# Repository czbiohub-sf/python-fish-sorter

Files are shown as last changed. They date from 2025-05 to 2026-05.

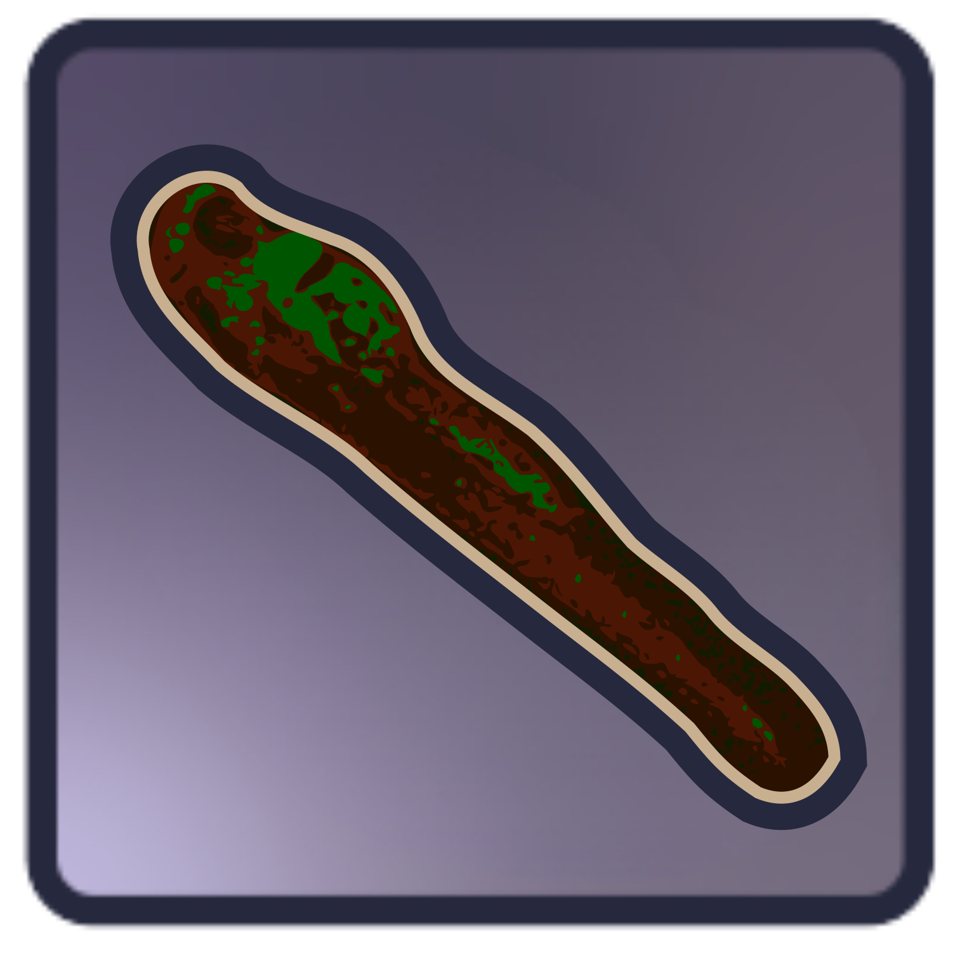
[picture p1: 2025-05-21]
executable/zebrari2.png

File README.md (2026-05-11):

# python-fish-sorter

This repository contains the Python application and custon __python-fish-sorter__ package for control of the Fish Sorter v2 using pymmcore+. Includes image acquisition and processing tools, such as mosaic capture/stitching. 

The Fish Sorter is a custom-built system for automated screening and selection of zebrafish embryos and larvae with desired features of interest. The system is built around a commercial inverted epi-fluorescent microscope for fish imaging, plus additional custom hardware for fish retrieval. 

The fish sorter was developed by the CZ Biohub SF Bioengineering and Jacobo groups.

Maintenance of this repo is the responsibility of Diane Wiener. Plese direct any communication via creation of an Issue at the project repo [here](https://github.com/czbiohub-sf/python-fish-sorter/issues).

This source describes Open Hardware, which is licensed under the CERN-OHL-W v2. Software is licensed under BSD 3-Clause.

Copyright 2025, Chan Zuckerberg Biohub San Francisco.

## Installation with uv

This package uses [uv](https://docs.astral.sh/uv/?utm_source=chatgpt.com) to manage reproducible installs and package dependencies.

The ground truth package lock is based on the software installed for the fish sorter v2 instrument running Windows with Python 3.12.0. The pinned versions are frozen in pyproject.toml + uv.lock.

1. Prerequisites

  * Python 3.12.0 installed on your system.

  * [uv](https://docs.astral.sh/uv/?utm_source=chatgpt.com)

    * Mac/Linux
      ```
        curl -LsSf https://astral.sh/uv/install.sh | sh
      ```
    * Add to PATH if needed
      ```
      echo 'export PATH="$HOME/.local/bin:$PATH"' >> ~/.zprofile
      ```

    * Windows (PowerShell)
      ```
      winget install --id=astral-sh.uv --source=winget -e
      ```
    * Restart PowerShell or add $HOME\.local\bin to PATH

2. Clone the repository

    Clone into your preferred directory (e.g. ~/Documents/GitHub):

    * Mac/Linux
      ```
      cd ~/Documents/GitHub
      git clone https://github.com/<your-org-or-username>/python-fish-sorter.git
      cd python-fish-sorter
      ```

    * Windows (PowerShell)
      ```
      cd $env:USERPROFILE\Documents\GitHub
      git clone https://github.com/<your-org-or-username>/python-fish-sorter.git
      cd python-fish-sorter
      ```
3. First-time setup
   ```
   uv sync
   ```
   
4. Running the project

    Inside the repo:
    ```
    uv run python fish_sorter/GUI/fish_sorter_app.py
    ```

5. Running one-off scripts outside the project

    If you keep helper scripts in a separate repo or folder (e.g. ~/Documents/GitHub/scripts), you can still run them using the fish_sorter environment:
    ```
    cd ~/Documents/GitHub/scripts
    uv --project ../python-fish-sorter run python my_script.py
    ```

    or with an absolute path:
    ```
    uv --project ~/Documents/GitHub/python-fish-sorter run python ~/Documents/GitHub/scripts/my_script.py
    ```

6. Updating dependencies

    Add a new package:
      ```
      uv add somepackage==1.2.3
      uv lock
      ```

    Commit both ```pyproject.toml``` and ```uv.lock```.

    Re-sync environment after changes:
    ```
    uv sync
    ```

7. Notes

    * Always use Python 3.12.

    * The fish sorter v2 instrument environment is the “ground truth.” If you change dependencies, re-lock on instrument first ```uv lock```.

## Local configuration
Follow setup for [napari-micromanager](https://github.com/pymmcore-plus/napari-micromanager) to configure to the specific microscope hardware. 
Micromanager configuration was configured with Micromanager 2.0 20240130. It is recommended to use thate nightly build:
* Use `fish_sorter/GUI/nmm.py` to test run napari-micromanager microscope control
* Use `fish_sorter/GUI/nmm_basic.py` to test run napari-micromanager microscope control with basic ancillary hardware control

An executable file, `fish_sorter.bat`, with icon, `zebrari2_Zbb_icon.ico` are located in the executable folder. 

In case of hardware or software installation differences, the following config files may need updating:
* In case of different Zaber stages, update the stage names in `fish_sorter/configs/hardware/zaber_config.json`
* In case of different micromanager configuration, update `MM_DIR` in `fish_sorter/paths.py`

NOTE: The stage control class in `zaber_controller.py` is intended to work with Zaber's binary library for compatibility with older stages. Newer stages may have compatibility issues with the binary library and require Zaber's ASCII library instead.

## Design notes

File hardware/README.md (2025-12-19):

# Hardware

Includes:
* CAD files for custom CNC components. See BOM (linked below) for material specifications
* CODESYS valve control code for use with Wago valve controllers
* Bill of Materials for off-the-shelf and custom parts

## Useful links
* [Onshape link](https://cad.onshape.com/documents/34757b4dd19d753c9017a122/w/cf503b114c56cf4eae313e87/e/65a73a903388aed1b68b23d7?configuration=default&renderMode=0&uiState=683a2d463e87190e9a255365) to view the full instrument in CAD

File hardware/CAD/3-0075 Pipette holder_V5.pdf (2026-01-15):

8

10

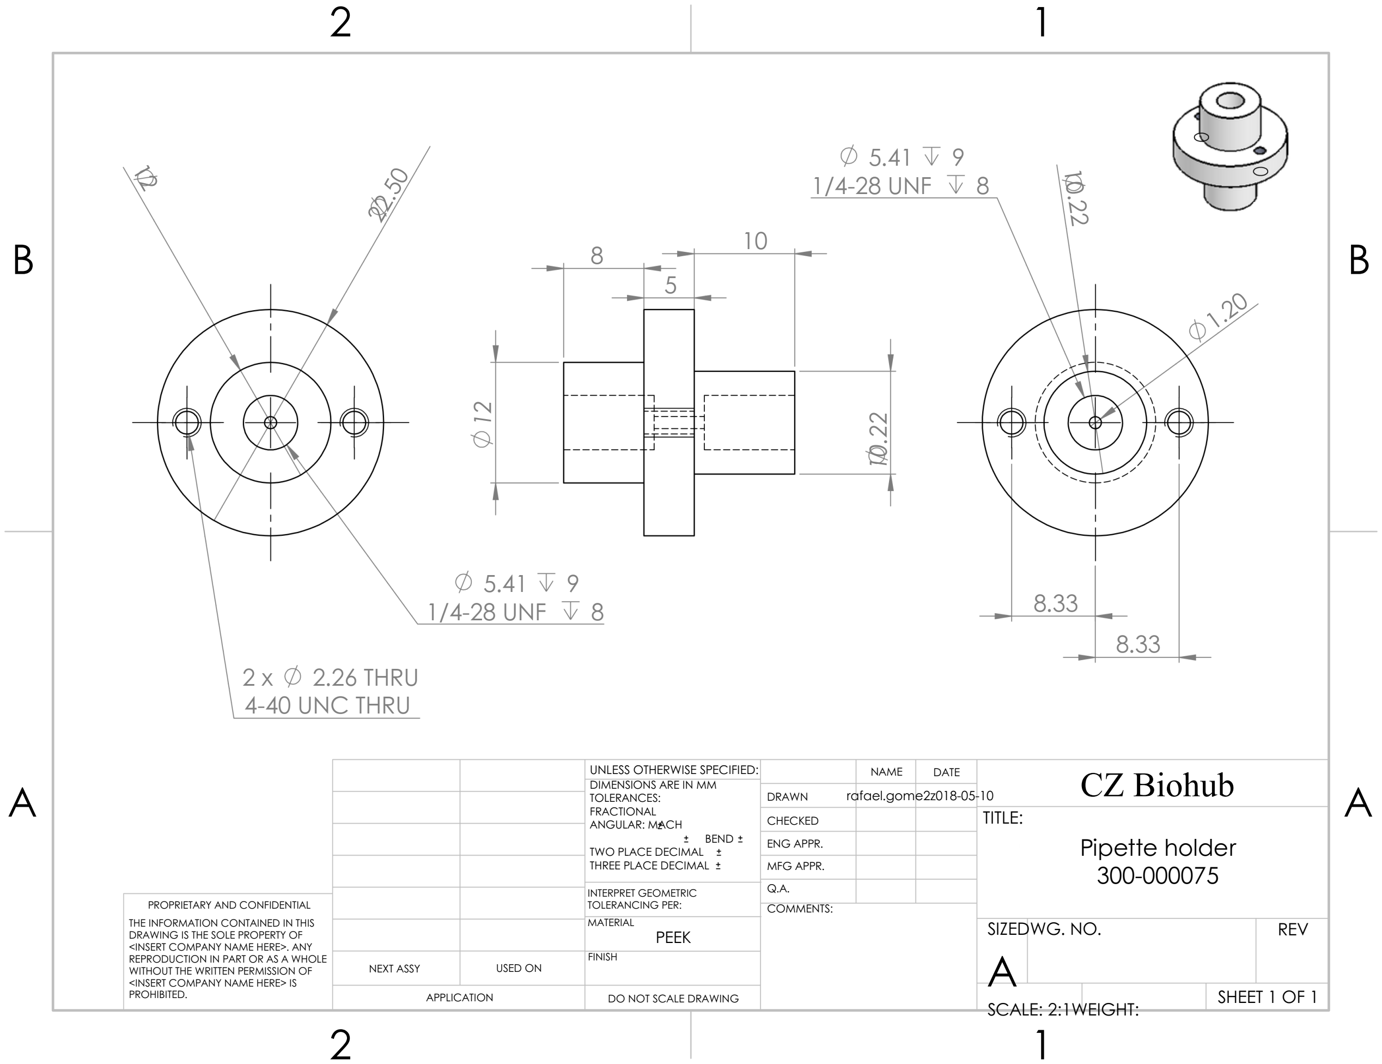
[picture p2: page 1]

22.50

12

5.41

# 1/4-28 UNF

# 2 x 2.26 THRU 4-40 UNC THRU

9
8

5

5.41

# 1/4-28 UNF

9
8

8.33
8.33

12

10.2

2

10.22

1.20

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
## PEEK

NEXT ASSY | USED ON
APPLICATION | DO NOT SCALE DRAWING

# TITLE:

SIZEDWG. NO.
A

# SCALE: 2:1WEIGHT:

# REV

# SHEET 1 OF 1

### rafael.gome2z018-05-10

UNLESS OTHERWISE SPECIFIED: DIMENSIONS ARE IN MM
TOLERANCES:
FRACTIONAL
ANGULAR: MACH

# CZ Biohub

BEND
TWO PLACE DECIMAL
THREE PLACE DECIMAL

DRAWN

CHECKED
ENG APPR.
MFG APPR.
Q.A.
COMMENTS:

NAME DATE

PROPRIETARY AND CONFIDENTIAL THE INFORMATION CONTAINED IN THIS DRAWING IS THE SOLE PROPERTY OF <INSERT COMPANY NAME HERE>. ANY REPRODUCTION IN PART OR AS A WHOLE WITHOUT THE WRITTEN PERMISSION OF <INSERT COMPANY NAME HERE> IS PROHIBITED.

FINISH

INTERPRET GEOMETRIC
TOLERANCING PER:
MATERIAL

# Pipette holder

300-000075

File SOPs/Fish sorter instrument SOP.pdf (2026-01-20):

### Fish sorter instrument SOP

Last Updated:

Jan 20, 2026

### Background

V2.0 of the fish sorter is a semi-automated zebrafish classification and selection instrument. It requires human labelled

fish classifications and selection criteria. The fish sorter functions for both embryos and larvae. This operation is for

use with the Fish Sorter instrument and using a napari interface for instrument control. This SOP is current for the

python-fish-sorter software tagged v2.1.1.

### Workflow

Load fish into an agarose array omnitray

See Casting agarose array v2 SOP

Loading a new pipette tip

Note that the tip can be reused many times

See Preparing pipette for Fish sorter v2 SOP

Setup the Fish Sorter Microscope

Contents

Background

Workflow

Load fish into an agarose array omnitray

Loading a new pipette tip

Setup the Fish Sorter Microscope

Start the Fish Sorter

Set up Instrument to image fish

Stitch Mosaic and Classify Fish

Pick fish

Collect Fish and Shut down

Troubleshooting / Reset

Hardware:

General Restart / Next Experiment:

Restart from Classification:

Restart for Picking:

Exported/saved data

Images: {data folder}

Classification data: {data folder}/{date_time}_{file prefix}_classifications.csv

Picking parameters {data folder}/{date_time}_{file prefix}_pickable.csv:

Picking results: {data folder}/{date_time}_{file prefix}_picked.csv

Setup microscope

. Turn on all hardware:

a. light source
i. open the shutter prior to operation

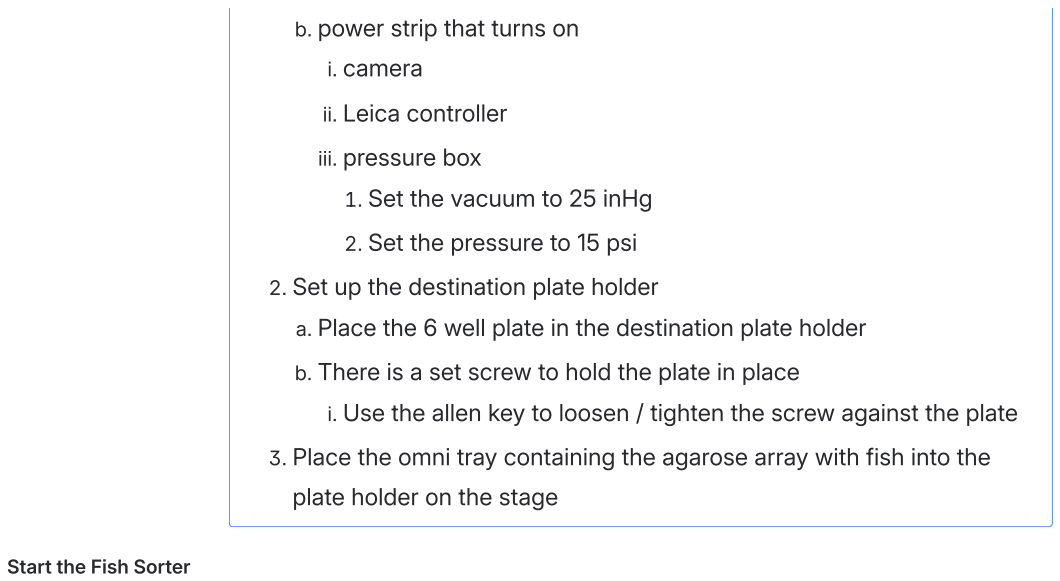
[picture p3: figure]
Start the Fish Sorter; b. power strip that turns on; i. camera; ii. Leica controller; iii. pressure box; . Set the vacuum to 25 inHg; . Set the pressure to 15 psi; . Set up the destination plate holder; plate holder on the stage
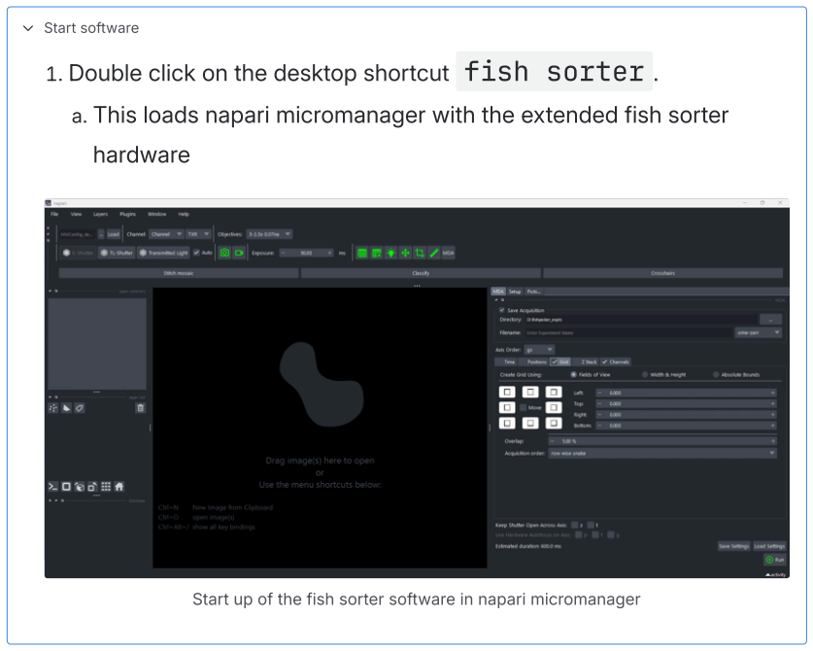
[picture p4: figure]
Start software; hardware

Set up Instrument to image fish a. Place the 6 well plate in the destination plate holder

b. There is a set screw to hold the plate in place
i. Use the allen key to loosen / tighten the screw against the plate

. Place the omni tray containing the agarose array with fish into the

. Double click on the desktop shortcut fish sorter .

a. This loads napari micromanager with the extended fish sorter

Start up of the fish sorter software in napari micromanager

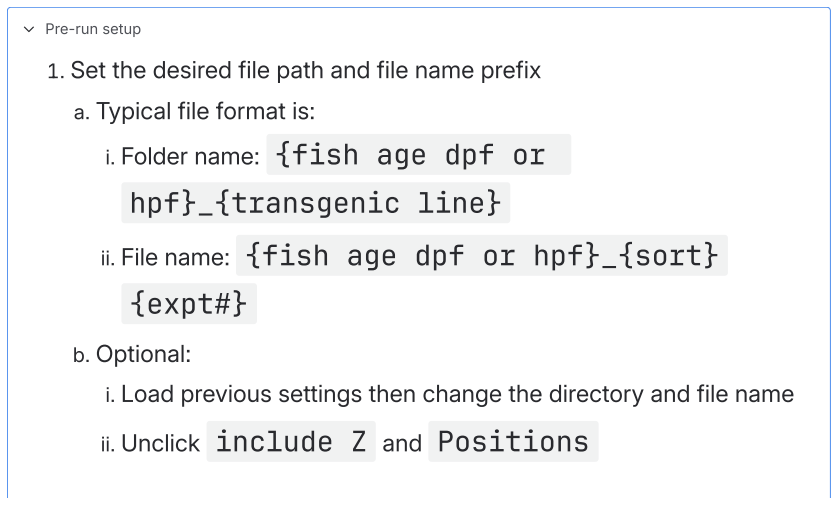
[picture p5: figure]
Pre-run setup; a. Typical file format is:; i. Folder name: {fish age dpf or; hpf}_{transgenic line}; {expt#}; b. Optional:; ii. Unclick include Z and Positions

. Set the desired file path and file name prefix

### ii. File name: {fish age dpf or hpf}_{sort}

i. Load previous settings then change the directory and file name iii. Check the grid positions for the top left and bottom right

. Move to each position

. Recenter as needed

. Click the corner to update

iv. Double check the channel settings for exposure and channels

c. In some cases, it may be desirable to image with brightfield (for

example, if the fluorescence is not bright enough to sufficiently

detect fish)

i. There are two methods to image in brightfield:

. With the brightfield condenser

a. This method will not allow for full remote operation after

imaging, because the pipette is not able to be positioned

over the objective in this case

b. Make sure the brightfield condenser arm is positioned over

the objective

### c. Click the Groups and Presets Table button

d. Adjust the TL-Ap (aperture) and TL-Light so that

the array is detectable

e. Note that when setting the MDA, the exposure and TLLight

values may need to be adjusted from the Preview values

f. Once imaging is complete, rotate the condenser arm away

from the objective, position the pipette over the objective

and calibrate it

. Pseudobrightfield with the side LED

a. Turn on the LED light
b. Move the pipette over the objective and calibrate it for

sorting

c. Move the collection plate stage over the microscope for

### imaging

d. Choose a suitable exposure time
d. In some cases, especially for embryos, it might be helpful to

acquire images at higher magnification

i. Change the objective with the Napari Micromanager

### Objective button

ii. The rest of the setup is the same

iii. It is important to do this before the Setup Picker tab

. If not, click New Experiment and repeat the setup

e. Note that we find it is faster to save the files locally to the

computer and then transfer to the shared drive

. If starting a new calibration Turn on Preview and

### Crosshairs

a. Calibrate the Top left and Bottom Right corners
i. Move to each position and click the specific corner when

calibrated

b. Make sure the pipette is over the objective if using fluorescent

channels for locating calibration points

. Click the Setup tab

a. Select the imaging and dispense plate arrays and fish type
b. Make sure the objective is correct prior to clicking Setup

### Picker

### c. Click Setup Picker

d. Note that this will save the MDA acquisition settings automatically

here

i. It is important that the magnification not be changed after this

point

. If it needs to be changed, click the New Experiment

button and adjust the setup parameters

. On the Picking tab

### a. Select Move to Swing

b. Move the pipette over
c. Tighten the swing arm to lock the pipette in place
d. Confirm the pipette stage arm is ready for software control:
i. Check that the LED light at the top of the stage is blue, and not

blinking red

If is blinking red, gently rotate the knob to move the stage

until you feel it click into a set position

. Calibrate the pipette

a. Adjust the pipette up or down using the move pipette button and

the input distance

b. Ensure the pipette is centered
c. For the the pick position, navigate to an area between wells in the

agarose array

d. Move the tip to just touch the top of the agarose array
e. Move up 50 um, move to a well, move back down 50 um
f. Move down 500 um and set the tip position

### g. Click the calibrate pick position

. Calibrate the dispense position

a. Move the dispense plate ensure the tip height for dispense makes

sense

. Bring to the center of the plate and focus on a fish

. Move the destination plate between the microscope and the pipette

### tip

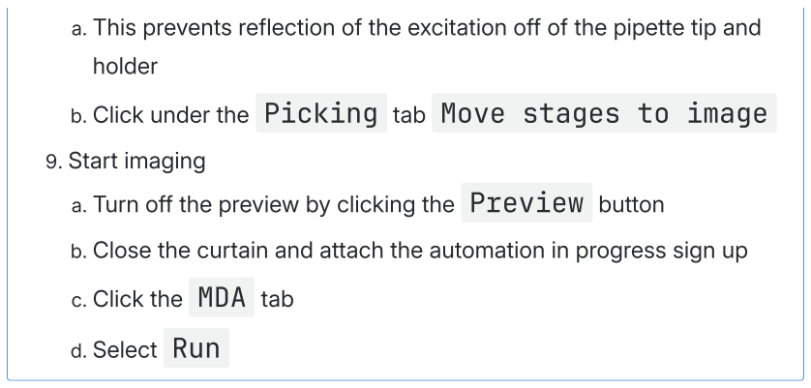
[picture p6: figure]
holder; . Start imaging; c. Click the MDA tab; d. Select Run

At this point, the system is walk-away and the remainder of the workflow can be completed using remote

computer control.

Stitch Mosaic and Classify Fish a. This prevents reflection of the excitation off of the pipette tip and

### b. Click under the Picking tab Move stages to image

a. Turn off the preview by clicking the Preview button
b. Close the curtain and attach the automation in progress sign up

Classification

. Mosaic stitching and loading the classification GUI will automatically

run after the imaging finishes. If you need manual controls, follow the

steps below:

### a. Click Stitch Mosaic

i. It takes a little bit, so wait or check the command line for status

### b. Click Classify

i. At any point it is possible reset the view to the full mosaic by

clicking the home button to center everything

. After the classification GUI has loaded, there should be only layers

for the mosaics of the imaged channels and Well Locations layer

. Click on the layers to change the contrast fluorescence intensity

a. Right click the contrast bar to make a big slider bar

. Find Fish

a. Choose either a specific channel, or the sum of the intensity
b. Set the Sigma to 1 and click Find Fish
i. Check whether it found the fish well enough or not

ii. Repeat if needed if not all of the fish are selected or there are

too many wells selected by adjusting the Sigma, typically

reducing the value

. Start to classify fish

a. Make sure you select the Well Locations layer
b. Click in the Classification feature widget
c. Start to classify based on the hot keys
d. Notes:
i. Double check the head orientation for larvae

ii. You can select a well point and it will load that well crop image

Pick fish

iii. If you hit empty and multiple it will deselect the well, e.g. if you

navigate backward it will not cycle through that position under

the found fish toggle condition

iv. Classify whether the slot is empty, has multiple fish, or only one

fish (singlet)

. Hotkeys: e , m , s

v. If the fish has fluorescence features, label it appropriately

. Hotkeys: Numeric ( 1 , 2 , …)

vi. Navigate through the wells

. It is not required to use the Find Fish algorithm to classify fish. With the navigation mode set to all wells you can navigate

through all wells and classify.

. Hotkeys: Right/left arrow

. Press T to switch between navigating through all of the fish

or the subset of fish found by the fish finding algorithm

. Under all well navigation mode, the right/left arrow keys move

to the next/previous well

a. If a feature classification is selected for a well, the well will

be automatically classified as a singlet

. It is possible to lasso several wells at once and bulk classify

. Under singlet navigation mode, the right/left arrow keys move

to the next/previous fish marked as a singled

a. Note: If a fish or well is reclassified as anything that is not a

singlet (empty, multiple, etc) it will be removed from the

singlet navigation group. The next well with a singlet fish

will be immediately displayed

vii. Press the Reset button to remove all found fish and

classifications

### . Hit Save Classification when done

a. This is at the bottom left in the same tab group as Finding

### Nemo

b. This saves an auto-generated classification for each well ( {file

### prefix}_classifications.csv ) in the data saving

folder

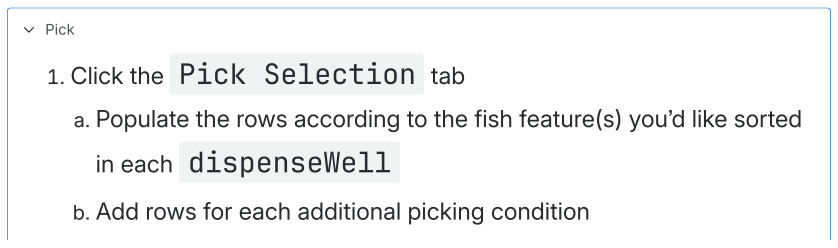
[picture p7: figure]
Pick; . Click the Pick Selection tab; in each dispenseWell

a. Populate the rows according to the fish feature(s) you’d like sorted
b. Add rows for each additional picking condition

Collect Fish and Shut down

### Troubleshooting / Reset

From almost every step in the process it is possible to recover from any issue that arises. In most cases this does not

require reloading the fish sorter napari window.

c. Click Save to save the pick selections
i. This saves an auto-generated picking file ( {file

prefix}_pickable.csv ) in the data saving folder

. (If not done already, or needed) adjust the pick and dispense heights

and click their corresponding buttons to update calibrate picking and

dispense position in Pick tab

a. If necessary, recalibrate the picking and dispense position by

adjusting the pick and dispense heights and clicking their

corresponding buttons to update

. If you want to watch live

a. Move dispense stages to home
b. Click the preview button and hide the other layers
i. Make sure to turn on one of the fluorescence channels for

pseudo brightfield

c. Click the crosshairs and zoom to the desired size

### . Click Full Pick!

. If you need to pause picking, click the Pause Picking button,

and then Resume when desired

a. This will restart from the current location in the pick list

. If you need to stop picking, click the Stop Picking button

a. If you click Full Pick! again, it will start from the beginning

of the pick list

Shutdown

. Move the pipette to the Swing position

. Exit the program

. Shut off the lamp

. Toggle the power switch button

. Remove the plates of picked fish and agarose mold

. Rotate the pipette arm away from the objective

. To keep dust off the objective, place a blank plate in the plate holder

. Return the agarose mold to the refrigerator after removing any

remaining fish

Hardware:

Hardware issues

If the dispense stages fail to move properly, or are not responding,

### press the Move Dispense Stages to Home and then

Move Dispense Stages to Image .

If they still do not move, click Reset Hardware and see if

the stages move then

Check that the LED lights at the back of the stage are lit

If the pipette fails to move properly, is only moving in one direction,

or fails to respond

Check that the LED light at the top of the stage is blue, and not

blinking red

If is blinking red, gently rotate the knob to move the stage until

you feel it click into a set position

Check if it now will move with the software

If it will not move down but will move up

Turn off the live preview, if it is on

Click the Pipette Down button

Toggle to the terminal window and read the current position

setting

If it is at 75 mm, then the pipette is at the travel limit

Contact BioE for support

For all else, click the Reset Hardware button and see if the

pipette moves.

If the pneumatics are not operating properly

If the fish are not being picked properly, check the pick height

position

Make sure that the pipette will slightly drag on the top surface of

the agarose. There should be some lag in the movement of the

pipette as the stage moves

Check the pick height is 500 um below the height of the agarose

If you moved the pipette up 50 um to move into the well, be

sure to move the pipette 550 um down from that point

Use the Single Pick option to check if a fish can be picked

Navigate to a fish

Click Move to Pick Position

Click Single Pick

The fish should be aspirated

At this point, either

dispense the fish into the destination plate

### Click the Move to Dispense Position

Click Expel twice

move the stage to the far edge of the plate, outside of the well

array

Click Expel twice

If the fish are still not picked properly, rotate the pipette away from

the objective

### Click the Toggle Pressure Valve

Ensure that there is a steady air stream coming from the tip

Click Toggle Pressure Valve again to stop the flow

If there was a steady stream of air, check picking a single fish

again

Check the Draw / Expel by moving to the outside of the well array

Move the pipette to the liquid surface

Click Draw

Check that liquid was aspirated

Move the pipette up

Click Expel

Check that the liquid was expelled

If it is still not possible to aspirate / dispense fish, replace the tip

Note that Reset Hardware maintains all experiment

parameters, and does not require New Experiment setup

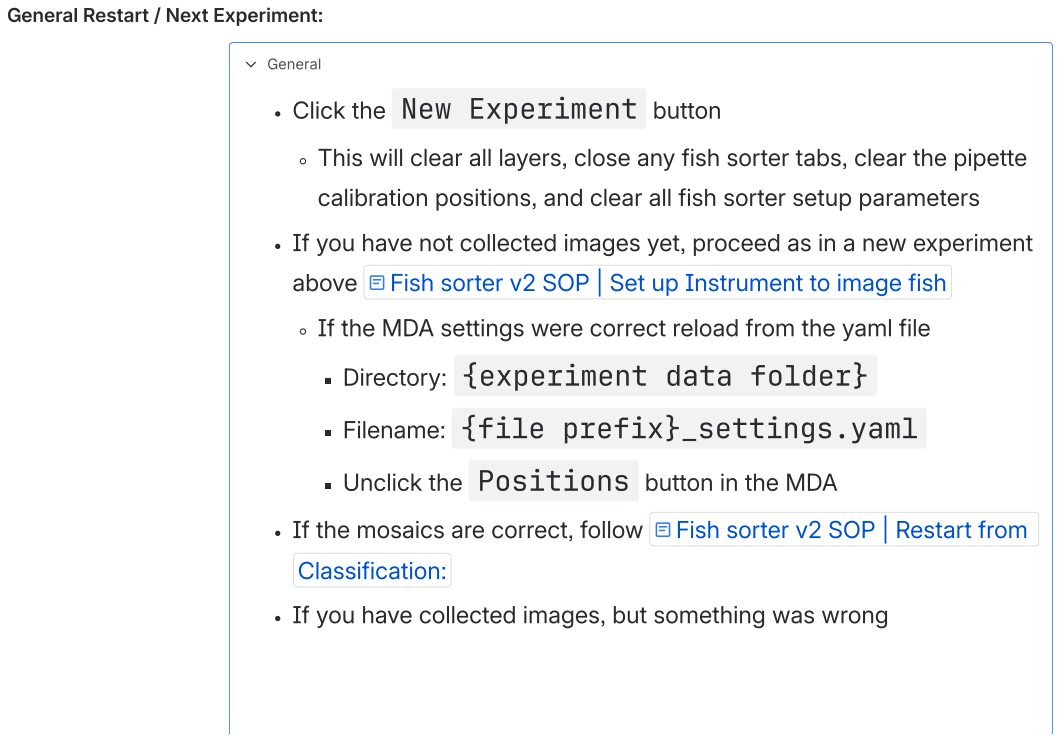
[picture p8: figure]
General Restart / Next Experiment:; General; Click the New Experiment button; above; Directory: {experiment data folder}; Filename: {file prefix}_settings.yaml; Unclick the Positions button in the MDA; If the mosaics are correct, follow; Fish sorter v2 SOP | Restart from; Classification:

This will clear all layers, close any fish sorter tabs, clear the pipette

calibration positions, and clear all fish sorter setup parameters

If you have not collected images yet, proceed as in a new experiment

If the MDA settings were correct reload from the yaml file

If you have collected images, but something was wrong

Fish sorter v2 SOP | Set up Instrument to image fish (https://czbiohub.atlassian.net/wiki/spaces/FP/pages/4476076291/Fish+sorter+v2+SOP)

Delete the previous ome.zarr folder and mosaics (anything

marked .tif )

If the MDA values are desired,

Reload the MDA settings from the yaml file

### Directory: {experiment data folder}

### Filename: {file prefix}_settings.yaml

Make adjustments, as needed, to the MDA settings

Unclick the Positions button in the MDA

Delete the .ome.zarr from the filename

It will reappear, but if it is not deleted it can get appended a

second time

Input the setup sorter parameters and click Setup Picker

If you had previously calibrated the pipette, you can recalibrate

### by pressing the Move to Pick Position / Move to

Dispense Position and once the pipette is done

### moving press the Calibrate Pick Postion /

### Calibrate Dispense Position button respectively

Click Run on the MDA

Otherwise, setup the MDA values as above

If for the new experiment the directory and filenames stay the

same as before, delete the .ome.zarr from the filename

It will reappear, but if it is not deleted it can get appended a

second time

### Fish sorter v2 SOP |

Set up Instrument to image fish (https://czbiohub.atlassian.net/wiki/spaces/FP/pages/4476076291/Fish+sorter+v2+SOP)

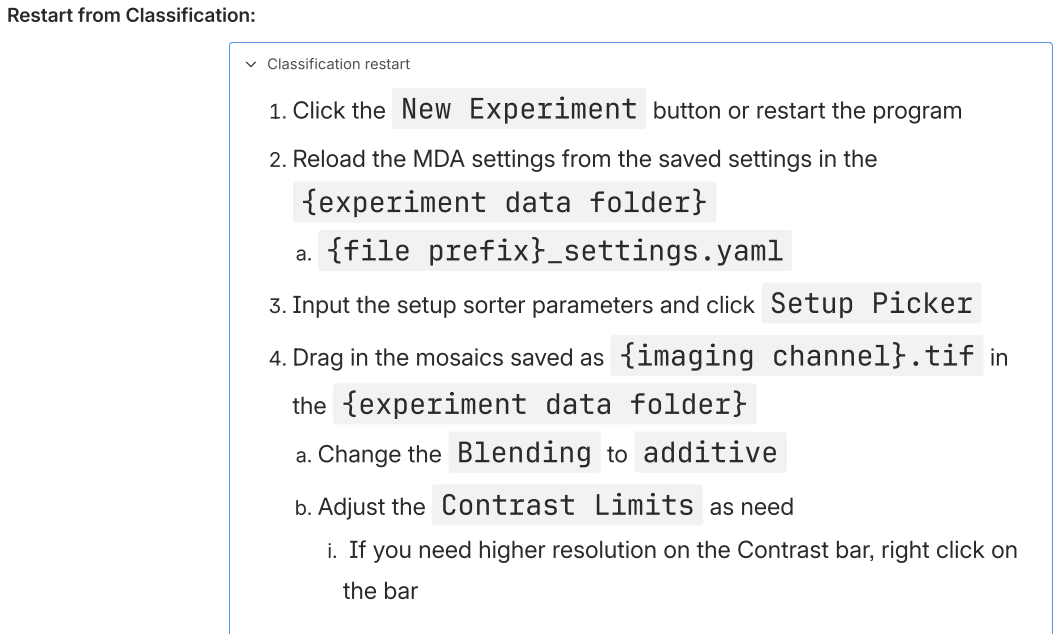
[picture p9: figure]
Restart from Classification:; Classification restart; {experiment data folder}; a. {file prefix}_settings.yaml; the {experiment data folder}; a. Change the Blending to additive; b. Adjust the Contrast Limits as need; the bar

. Click the New Experiment button or restart the program

. Reload the MDA settings from the saved settings in the

. Input the setup sorter parameters and click Setup Picker

. Drag in the mosaics saved as {imaging channel}.tif in

i. If you need higher resolution on the Contrast bar, right click on

Restart for Picking:

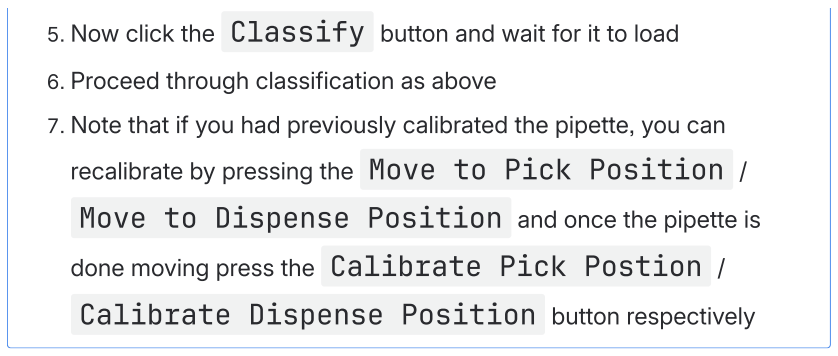
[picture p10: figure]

### Exported/saved data

. Now click the Classify button and wait for it to load

. Proceed through classification as above

. Note that if you had previously calibrated the pipette, you can

recalibrate by pressing the Move to Pick Position /

### Move to Dispense Position and once the pipette is

### done moving press the Calibrate Pick Postion /

### Calibrate Dispense Position button respectively

Picking restart

### . Navigate to the {experiment data folder}

a. Confirm that the classification and pick selection files exist and

contain accurate information

i. If so, continue on

ii. If not, follow the steps for

. Click the New Experiment button

. Reload the MDA settings from the saved settings in the

### {experiment data folder}

### a. {file prefix}_settings.yaml

. Input the setup sorter parameters and click Setup Picker

### . Click Classify

a. Note that it is not required to load the mosaics, if the classification

and pick selection parameters (csv files) already exist

b. This loads the array plate location settings and is required for

### picking

. Calibrate the Pipette

a. If you had previously calibrated the pipette, you can recalibrate by

### pressing the Move to Pick Position / Move to

Dispense Position and once the pipette is done moving

### press the Calibrate Pick Postion / Calibrate

### Dispense Position button respectively

### . Click Full Pick

### Fish sorter v2 SOP | Restart from Cl

assification: (https://czbiohub.atlassian.net/wiki/spaces/FP/pages/4476076291/Fish+sorter+v2+SOP)

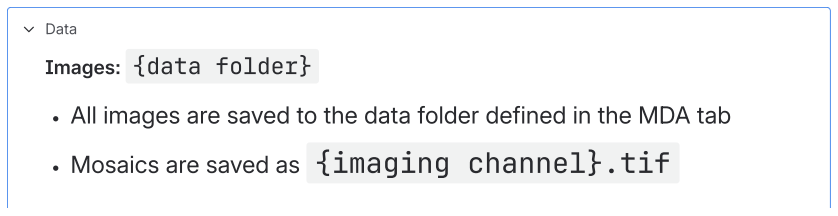
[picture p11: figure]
Data; Images: {data folder}

All images are saved to the data folder defined in the MDA tab

Mosaics are saved as {imaging channel}.tif

Data is saved locally and then can be moved to BRUNO, which

### should be /hpc/instruments/bioe.fishsorter

Classification data: {data folder}/{date_time}_{file

prefix}_classifications.csv

CSV with classification based on user selection

Headers/feature names are generated based on features

### defined in pick_type_config.json

Picking parameters {data folder}/{date_time}_{file

prefix}_pickable.csv :

CSV specifying dispense well for each set of fish features based on

GUI inputs

Headers/feature names are generated based on features

### defined in pick_type_config.json

Picking results: {data folder}/{date_time}_{file

prefix}_picked.csv

CSV with classification based on user classification and picking

parameters

Each time Full Pick! is run a new file will be generated

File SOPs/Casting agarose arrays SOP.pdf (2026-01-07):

Casting agarose arrays v2 SOP

Background

Agarose arrays of slots are used to ensure the zebrafish lie in a regular pattern. These agarose arrays need to be cast

prior to fish sorting experiments.

There are two molds, one for sorting embryos and one for sorting larvae. The embryo mold contains a grid of 400 wells.

The larvae mold contains a grid of 595 wells. The top left and bottom right wells for both molds are triangular shaped.

These are used to locate the corners for calibration of the fish sorter instrument. The remaining wells are circular

embryos and rectangular for larvae.

Agarose arrays can be reused several times if stored properly (ie. in a fridge, filled with E3 media and covered with a lid

to prevent drying out). Agarose arrays should be replaced when any of the following is observed:

Damage

Shrinkage or change in shape (due to array drying out)

Cloudiness (which hurts imaging quality)

Materials

Nunc™ OmniTray™ Single-Well Plate (https://www.thermofisher.com/order/catalog/product/242811)

Male grating mold (see top of document for link/ID for latest version)

Bio-Rad Certified Molecular Biology Agarose, Cat # 1613102 is confirmed to produce successful

molds for arraying and imaging of fish)

E3 media

25 mL serological pipette

Optional) Razor blade

Molds:

Current male molds: V53 - Zebrafish sorting

Larvae: Use configuration Large - sorting - 2 corner

Embryo: Use configuration Medium-sorting-2 Corner

Thermo Fisher Nunc OmniTray (https://cad.onshape.com/documents/3c4be6ac45abd2ebb576558b/v/e634d468ee704eb9569a6afe/e/95e680917df9c3df151722a0)

Agarose powder (https://www.bio-rad.com/en-us/sku/1613102-certified-molecular-biology-agarose-500g?ID=1613102)

Version 53 Fish Sorter v2, Left: embryo mold, Right: larvae mold

Workflow

Cleaning mold and OmniTray

The OmniTrays are reusable. Both the mold and OmniTray should be cleaned before use:

. Rinse the mold and OmniTrays with Di-water

. Dry with house dry compressed air

a. Be sure to dry the mold very well

. Spray the OmniTray with 70% ethanol

. Dry with house dry compressed air

Casting agarose array

. Make a 2% agarose solution, dissolved in E3 media

a. Typically prepare 100 mL of 2% agarose:
i. weigh 2 g agarose

ii. add 100 mL E3 media

iii. heat in the microwave to dissolve

. Aspirate 15 mL agarose solution with the serological pipette

a.If you have extra agarose, store in a sealed jar in the incubator set to 68 deg C so the agarose stays liquid and can

be used in future casts

. Dispense the agarose solution in the OmniTray

. Wet the mold in the agarose (to minimize bubbles on mold surface while casting)

. Place the mold over the agarose solution

. Check for bubbles by lifting the OmniTray and viewing the agarose/mold through the clear bottom surface

a.If there are bubbles, lift the mold out of the agarose and place the mold down again

b. Repeat as necessary

. Place a heavy item (eg. E3 media jar) over the mold

. Set agarose for 15 minutes

Removing the mold

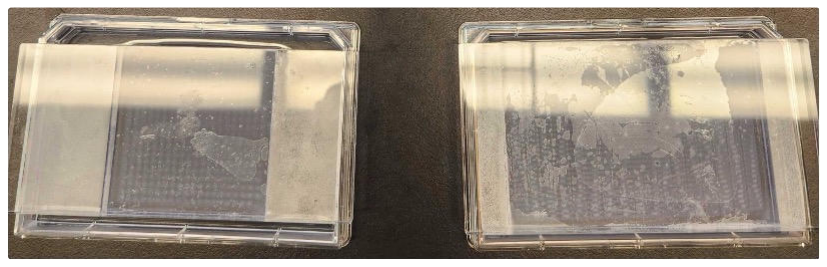
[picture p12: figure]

. Add E3 media into the plate, with the male mold still in place. This make it easier to separate the mold from the

agarose)

. Attempt to slowly lift the mold, starting from one corner

a. Once a single corner is lifted, E3 media should flow between the mold and the agarose
b. The whole mold should then be easy to remove

. Optional) If it’s difficult to perform Step 2 without tearing the agarose, try the following:

a. Use a razor blade to separate the outer edges of the mold from the agarose
b. Repeat Step 2

Embryo and larvae molds in

. Cover with the OmniTray lid and store in the refrigerator until used

Storing agarose array

After experiments, fill the agarose array with E3 media and cover with the lid before storing in a fridge. This will prevent

the agarose from drying out.

Label each agarose array with the following:

Date

Male mold version and slot size (eg. S/M/L

Agarose solution percentage (eg. 2%) and media (eg. E3)

Unique identifier (eg. A, B, C, etc.) if multiple agarose arrays are cast on the same day

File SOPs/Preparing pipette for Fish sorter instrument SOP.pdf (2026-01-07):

### Preparing pipette for Fish sorter instrument SOP

### Background

The pipette is used to aspirate and dispense the zebrafish larvae and embryos. It is connected to the pneumatics system that

controls the pressure and vacuum. It is also mounted to a z-axis stage to raise and lower the pipette. The length of the pipette is

critical to properly aspirate the fish and also to prevent crashes of the instrument. Note the pipette length is confirmed for the fish

sorter v2 system. The length may vary from the v1 cell picker system. This is for use with the V53 - Fish Sorter v2

molds Casting agarose arrays v2 SOP .

The pipette can be reused several times. It should be replaced when any of the following is observed:

Damage (due to crashes, etc)

Clogging (rare)

Dirtiness

### Materials

Globe Scientific 51680, Micro Hematocrit Capillary Tube, PETG

0.85 x 1.55 x 75 mm

Capillary Tube, Microhematocrit, 100% PLASTIC, Blue Tip, Plain (https://www.globescientific.com/plastic-micro-hematocrit-capillary-tubes.html?psku=51680&cid=0)

IDEX P200 ferrule, Flangeless Ferrule ETFE, 1/428 Flat-Bottom, for 1/16" OD

IDEX H&S Store - Product Detail (https://www.idex-hs.com/store/product-detail/flangeless_ferrule_tefzel_etfe_1_4_28_flat_bottom_for_1_16_od_blue/p-200?search=true)

IDEX P202 male nut, Flangeless Male Nut Delrin®, 1/428 Flat-Bottom, 1/16" OD

IDEX H&S Store - Product Detail (https://www.idex-hs.com/store/product-detail/flangeless_male_nut_delrin_1_4_28_flat_bottom_1_16_od_red/p-202?search=true)

31208 SCP Pipette stabilizer with short paddle 1.5 mm OD tip configuration

Onshape (https://cad.onshape.com/documents/d7feb16a4959ddcf875270cc/w/a84112968388fb8ce58b8050/e/cb903d07f5d292da911a1183)

Ruler with cm

Razor blade

### Workflow

Remove old pipette

The IDEX P202 male nut and the 31208 SCP Pipette stabilizer are reusable

. | Move the pipette arm so that it can be rotated to the center of the microscope
. | Unscrew the P202 male nut from the pipette holder
. | Remove the pipette, keeping the P202 male nut
. | Remove the grey 31208 SCP pipette stabilizer from the pipette, keeping the stabilizer
. | The old pipette can be thrown away

Cut new pipette

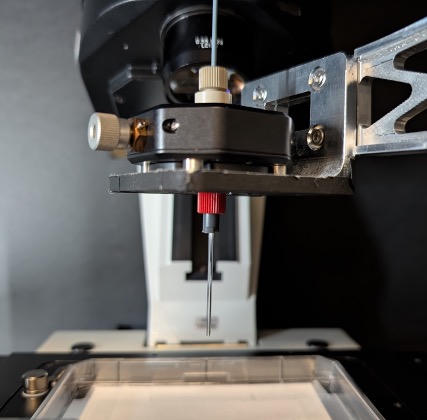
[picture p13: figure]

. Place the new new hematocrit capillary next to the ruler

a. The blue ring side should be at the 0 cm mark
b. The blue ring side is not the side to cut

. With the razor blade cut the capillary at the 65 cm line

a. It is important for the cut to be as clean and perpendicular as possible
b. The cut side is the side that will aspirate / dispense the fish

. Insert the blue ring side of the pipette into the IDEX P200 ferrule

a. The large OD flat part of the flange should be flush with the end of the pipette
b. A new ferrule should be used for each new pipette
c. The ferrule will be loose on the pipette to start, but after screwing into the pipette holder will crimp to the pipette

Insert new pipette

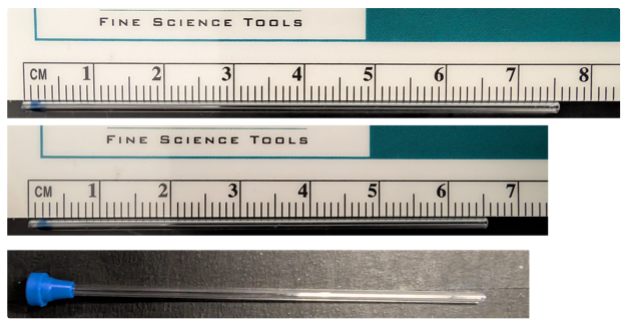
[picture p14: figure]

This step is like the reverse of the removal step above

. Insert the pipette into the IDEX P202 male nut

a. The large OD flat part of the ferrule should be flush with smaller OD, threaded side of the nut
b. Be careful when handling since the pipette may slide inside the ferrule

. Screw the IDEX P202 male nut into the pipette holder, making sure that the pipette has not fallen out

Mounted pipette

Assembled pipette | Exploded view of assembly

New pipette a. At this point the ferrule should be crimped to the pipette. It is fine to remove the pipette and from the male nut and reinsert it,

if need be

. Slide the grey 31208 SCP pipette stabilizer over the pipette tip and into the larger diameter side of the male nut

a. The stabilizer helps with minor adjustments of the pipette

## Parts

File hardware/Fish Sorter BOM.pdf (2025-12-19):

Item Number Description | | Vendor | PN | Qty | Notes
1 | Microscope | Leica | DM6000B | 1 | or equivalent such as DMI8
2 | HC PL FLUOTAR 2.5x/0.07 NA Objective | Leica | 506523 | 1
3 | N PLAN 5x/0.12 NA PH0 Objective | Leica | 506303 | 1
4 | Mercury arc lamp | Leica | EL6000 | 1
5 | Andor Zyla 4.2 sCMOS camera | Oxford Instruments | Zyla 4.2 | 1
6 | DAPI filter set | Chroma | 39000 | 1
7 | EGFP /FITC/ Cy2/ AlexaFluro 488 filter set | Chroma | 39002 | 1
8 | EYFP/ Venus/ Citrine filter set | Chroma | 39003 | 1
9 | TXR/ mCherry/ AlexaFluor 594 filter set | Chroma | 39010 | 1
10 | Cy5/ AlexaFluor 647/ Draq5 | Chroma | 39007
11 | Motion stages for collection plate, x | Zaber | T-LSQ150D | 1 | or equivalent
12 | Motion stages for collection plate, y | Zaber | A-LSQ150A-E01 | 1 | or equivalent
13 | Motion stage for pipette | Zaber | T-LSQ075B | 1 | or equivalent
14 | Motion stage data cable | Zaber | X-DC02 | 1
15 | Optical breadboard | Thorlabs | PBG2436F | 1
16 | Optical post platform for collection plate | Thorlabs | C1519 | 2
17 | Optical post for collection plate | Thorlabs | P8 | 2
18 | Optical post for collection plate | Thorlabs | P1.5 | 2
19 | Pipette XY mount | Thorlabs | CXY1 | 1
20 | Cage rods for Pipette XY mount | Thorlabs | ER1 | 4
21 | Optical post for Pipette | Thorlabs | DP14A | 1
22 | Pipettor fluidic nut mount (with modification) | Thorlabs | SM1A62 | 1 | Requires machined modifications, see mechanical drawings
23 | Valve controller terminal | Wago | 750-881 | 1
24 | Valve controller block | Wago | 750-504 | 1
25 | Valves | Festo | VOVK-BT6-M32C-MN-1H5ZP-FB | 2
26 | Valve manifolds | Festo | VABS-C12-6-B-M3 | 2
27 | Festo Push-In to Threaded Straight Fitting 4mm OD Tubing | Digikey | QSM-M5-4-I | 4
28 | Festo Push-In to Threaded Straight Fitting 4mm OD Tubing | Digikey | QSM-M3-4-I | 2
29 | Aluminum enclosure for pneumatics controller | Digikey | 1401E | 1
30 | Mounting bracket for Wago | McMaster-Carr | 8961K102 | 1
31 | Precision pressure regulator 0-30psi, SMC Corp. AR20-N01H-1Z-D | Grainger | 807FP6 | 1
32 | Precision vacuum regulator 30-0inHg, SMC Corp. IRV10-N07BG | Grainger | 30J548 | 1
33 | In-line vacuum filter, SMC ZFC5D-B | Grainger | 30J537 | 1
34 | Panel-mount pressure gauge, 0-30psi, 1.5" dia. | McMaster-Carr | 4000K719 | 1
35 | Panel-mount vacuum gauge, 30-0inHg, 1.5" dia. | McMaster-Carr | 4002K25 | 1
36 | Toggle switch, panel mount | Digikey | 360-M2011SS1W01/CUL-N983-ND | 1
37 | LED indicator, green, panel-mount, 24Vdc | Digikey | 679-2842-ND | 1
38 | Power connector, panel-mount, 2.5mm x 5.5mm | Digikey | CP-064B-ND | 1
39 | Line cord for power adapter, 3 conductor, US plug | Digikey | AC30UNA-R | 1
40 | Desktop power adapter, 24Vdc, 36W | Digikey | 993-1447-ND | 1
41 | 3-Way Stopcock, PC, Female x Female x Male Locking | Cole-Parmer | EW-48523-28 | 1
42 | Luer to Hose Barb Fitting, Polypropylene, Male Luer Lock x 1/16" ID; 10/Pk | Cole-Parmer | EW-50110-11 | 1
43 | Luer to Hose Barb Fitting, Polypropylene, Female Luer x 3/32" ID; 10/Pk | Cole-Parmer | EW-50109-70 | 1
44 | 1/4" OD hardwall tubing | McMaster-Carr | 5548K966-25ft | 1
45 | 1/4" OD firm tubing | McMaster-Carr | 5648K74-25ft | 1
46 | Tubing between pipette and pneumatics controller (0.01" ID) | McMaster-Carr | 51085K44-5ft | 1 | 37" required between pipette and pneumatics box
47 | 5/32" OD firm tubing | McMaster-Carr | 5648K68-25ft | 1
48 | 1/8" OD firm tubing | McMaster-Carr | 5648K67-5ft | 1
49 | Elbow Assembly PEEK - 1/16" OD | IDEX Health & Science | P-430 | 1
50 | Flangeless Ferrule ETFE, 1/4-28 Flat-Bottom, for 1/16" OD Blue | IDEX Health & Science | P-200X | 1
51 | Flangeless Nut Delrin®, Short, 1/4-28 Flat-Bottom, for 1/16" OD Black | IDEX Health & Science | P-208 | 2
52 | Flangeless Male Nut Delrin®, 1/4-28 Flat-Bottom, 1/16" OD Red | IDEX Health & Science | P-202 | 1
53 | Flangeless Nut PEEK, 1/4-28 Flat-Bottom, for 1/8" OD Natural | IDEX Health & Science | P-330 | 1
54 | Flangeless Ferrule ETFE 1/4-28 Flat-Bottom, for 1/8" OD Yellow | IDEX Health & Science | P-300 | 1
55 | Push to Connect Straight Adapter, for 1/4" Tube OD x 3/8 NPT Male | McMaster-Carr | 5779K111 | 2
56 | Push to Connect Through-Wall Connector for 1/4" Tube OD | McMaster-Carr | 5779K677 | 2
57 | Push to Connect Through-Wall Connector for 5/32" Tube OD | McMaster-Carr | 5779K676 | 1
58 | Push to Connect Straight Adapter, for 1/8" Tube OD x 1/8 NPT Female | McMaster-Carr | 5779K123 | 2
59 | Push to Connect Straight Adapter, for 1/8" Tube OD x 1/8 NPT Male | McMaster-Carr | 5779K102 | 2
60 | Push to Connect 90 Degree Elbow Connector, for 1/4" Tube OD | McMaster-Carr | 5779K24 | 1
61 | Push to Connect Tee Connector, for 1/4" Tube OD | McMaster-Carr | 5779K34 | 2
62 | Push to Connect Adapter, 1/8" Stem OD, for 1/4" Tube OD | McMaster-Carr | 5779K362 | 2
63 | Push to Connect Adapter, 1/4" Stem OD x 5/32" Tube OD | McMaster-Carr | 5779K712 | 2
64 | Push to Connect 90 Degree Elbow Reducer, for 1/4" x 1/8" Tube OD | McMaster-Carr | 5779K661 | 2
65 | Pipette Micro Hematocrit Capillary Tube, PETG, 0.85 x 1.55 x 75 mm | Globe Scientific | 51680 | 1
66 | 3/16" cast acrylic | McMaster-Carr | 8560K211 | 1 | For laser cut parts
67 | Collection plate holder, CNC machined aluminum 6061 | External Machining | 3-1973 | 1
68 | Pipettor bracket, CNC machined aluminum 6061 | External Machining | 3-1953 | 1
69 | Pipettor arm, CNC machined aluminum 6061 | External Machining | 3-1954 | 1
70 | Pipettor rotation clamp, CNC machined aluminum 6061 | External Machining | 3-0137 | 1
71 | Non-piezo pipette holder, CNC machined PEEK | External Machining | 3-0075 | 1
72 | Embryo male mold, SLA 3D printed | Internal Fabrication | 3-1488-M2 | 1 | Dental LT Clear V2 resin
73 | Embryo mold mount, laser cut cast acrylic | Internal Fabrication | 3-1489-M2 | 1 | 3/16" clear acrylic
74 | Embryo mold holder, laser cut cast acrylic | Internal Fabrication | 3-2057-M2 | 1 | 3/16" clear acrylic
75 | Larvae male mold, SLA 3D printed | Internal Fabrication | 3-1477-L2 | 1 | Dental LT Clear V2 resin
76 | Larvae mold mount, laser cut cast acrylic | Internal Fabrication | 3-1622-L2 | 1 | 3/16" clear acrylic
77 | Larvae mold holder, laser cut cast acrylic | Internal Fabrication | 3-1623-L2 | 1 | 3/16" clear acrylic
78 | Pipette stabilizer, SLA 3D printed | Internal Fabrication | 3-1208 | 1 | Tough 2000 resin

## Fish Sorter Bill Of Materials

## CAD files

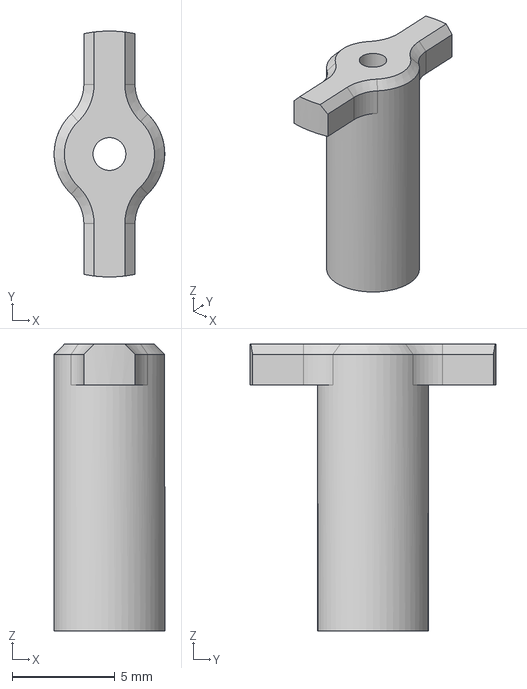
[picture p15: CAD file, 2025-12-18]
hardware/CAD/3-1208_SCP Pipette stabilizer with short paddle_Main.step
5.40 x 12.0 x 14.0 mm

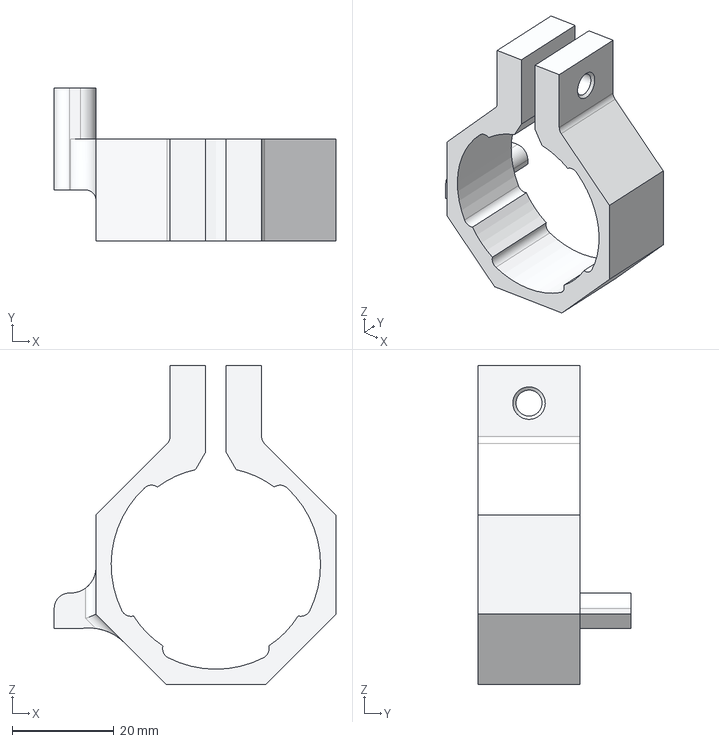
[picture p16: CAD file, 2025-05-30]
hardware/CAD/3-0137 Pipettor rotation clamp_V1.step
55.3 x 30.0 x 62.7 mm

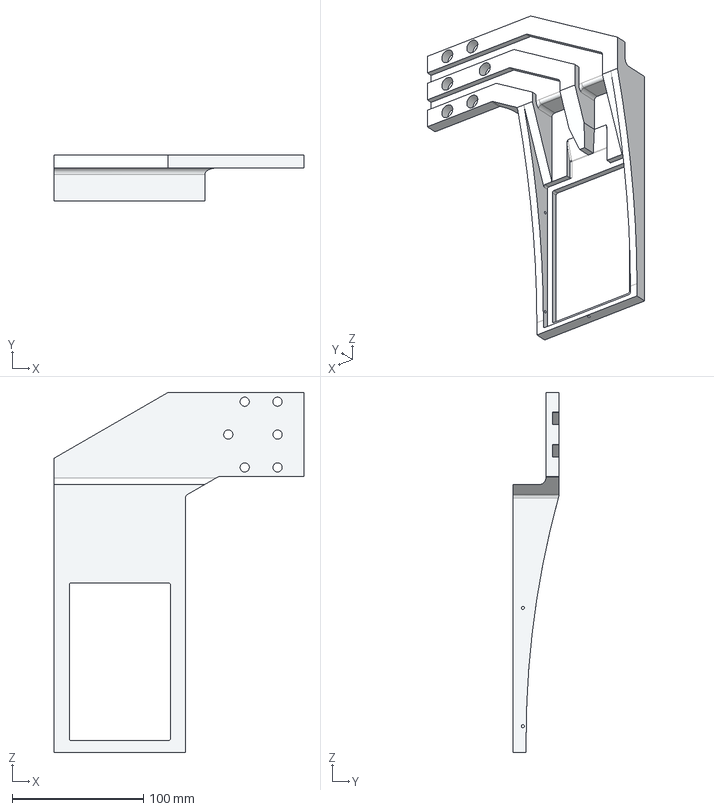
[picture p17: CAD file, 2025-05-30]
hardware/CAD/3-0073 Plate Chiller Arm_V1.step
190.0 x 35.0 x 273.9 mm

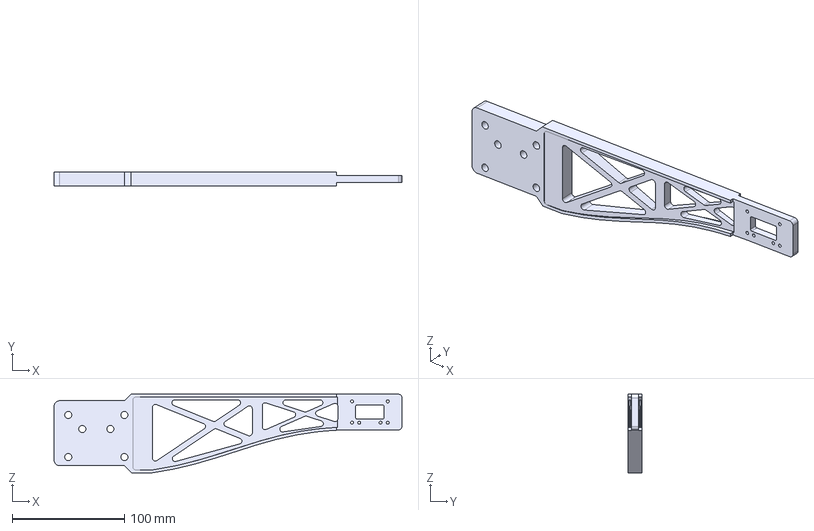
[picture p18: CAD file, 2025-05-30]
hardware/CAD/3-0054 SCP Pipettor arm_V1.step
309.9 x 12.7 x 70.0 mm

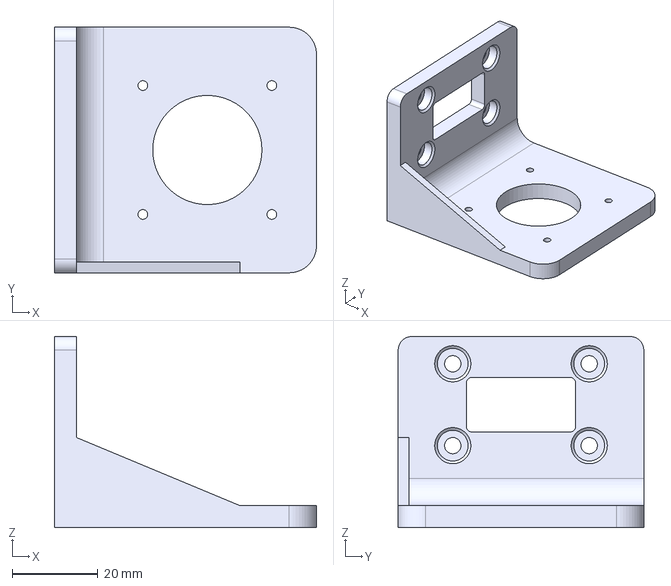
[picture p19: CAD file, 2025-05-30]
hardware/CAD/3-0053 SCP Pipettor L-bracket_V28.step
61.0 x 57.1 x 44.5 mm

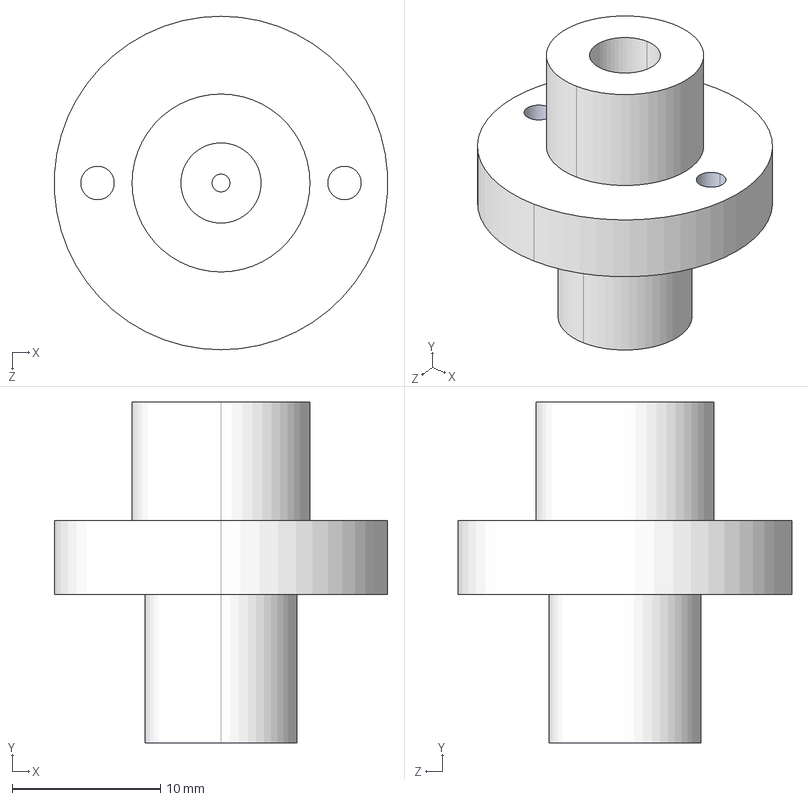
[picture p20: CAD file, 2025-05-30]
hardware/CAD/3-0075 Pipette holder_V1.STEP
22.5 x 23.0 x 22.5 mm

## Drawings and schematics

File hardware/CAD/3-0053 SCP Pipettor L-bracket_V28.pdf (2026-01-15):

2
1

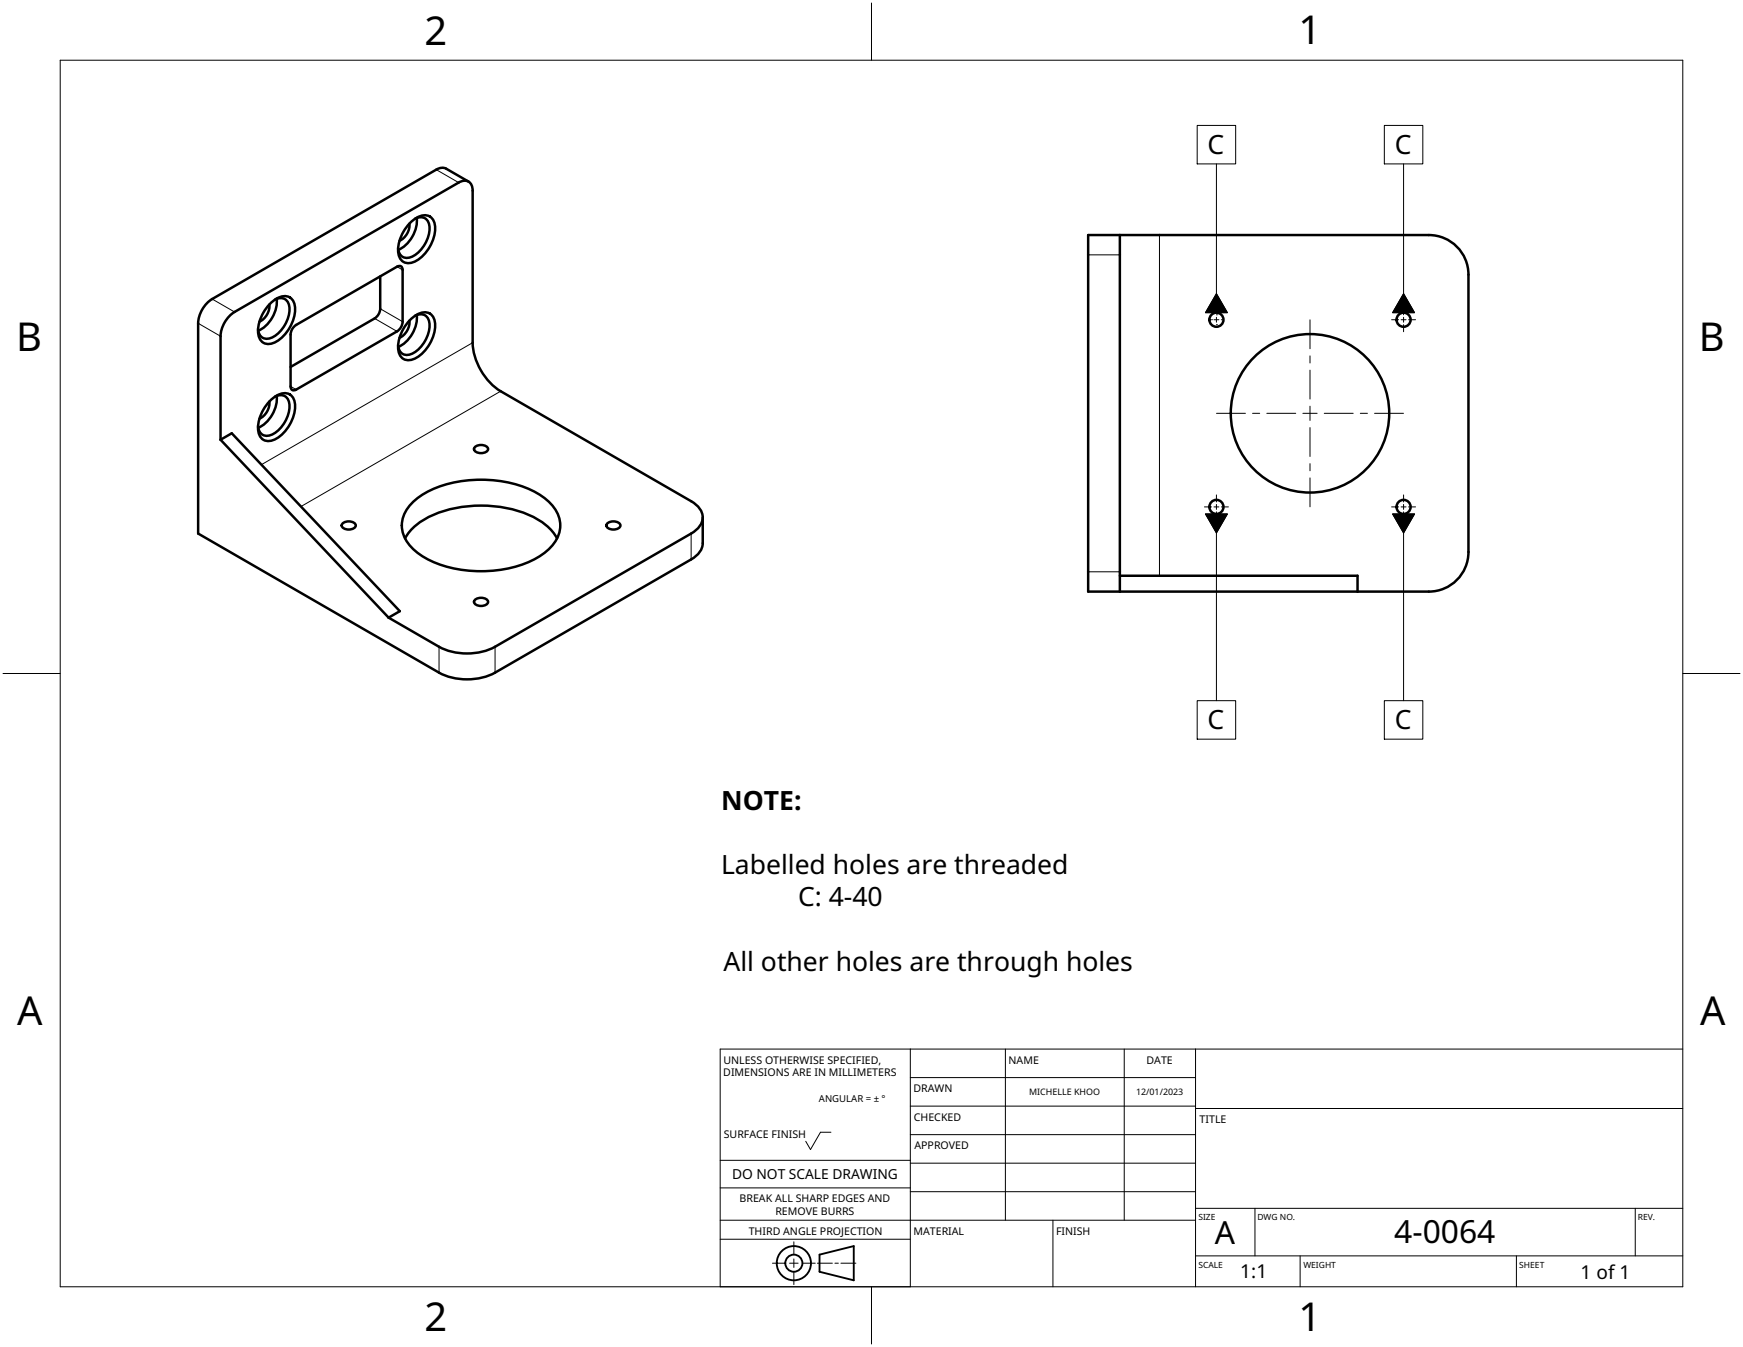
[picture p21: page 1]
MATERIAL; FINISH; NOTE:

Labelled holes are threaded

All other holes are through holes

UNLESS OTHERWISE SPECIFIED, DIMENSIONS ARE IN MILLIMETERS ANGULAR = ± ° SURFACE FINISH | | NAME | DATE

DRAWN | MICHELLE KHOO | 12/01/2023

CHECKED | | | TITLE

APPROVED

DO NOT SCALE DRAWING

BREAK ALL SHARP EDGES AND

REMOVE BURRS
THIRD ANGLE PROJECTION

SIZE A | DWG NO. 4-0064 | REV.

SCALE 1:1 | WEIGHT | SHEET 1 of 1

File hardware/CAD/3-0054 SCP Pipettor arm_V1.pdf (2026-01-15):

2
1

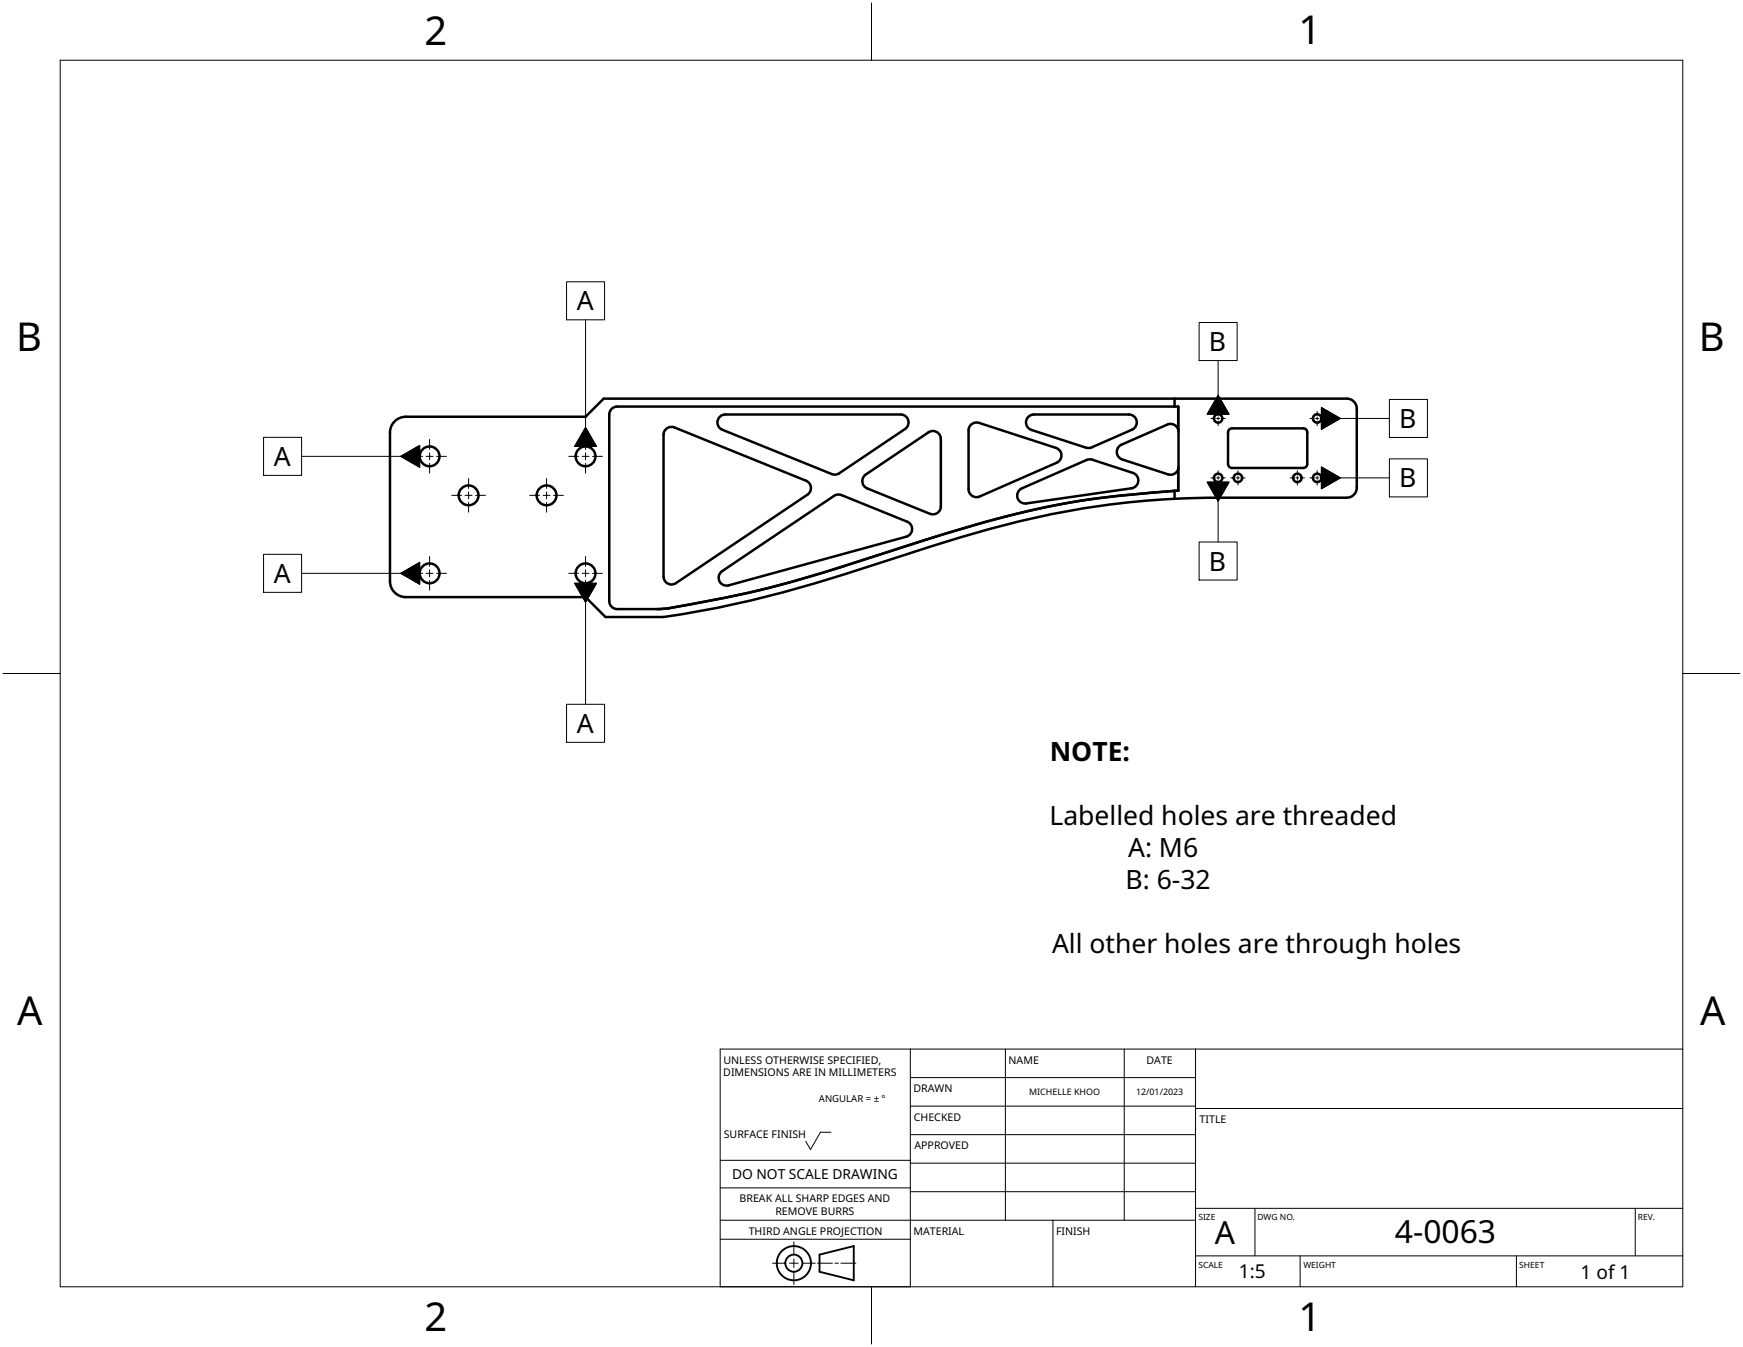
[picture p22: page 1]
MATERIAL; FINISH; NOTE:; Labelled holes are threaded A: M6 B: 6-32

All other holes are through holes

UNLESS OTHERWISE SPECIFIED, DIMENSIONS ARE IN MILLIMETERS ANGULAR = ± ° SURFACE FINISH | | NAME | DATE

DRAWN | MICHELLE KHOO | 12/01/2023

CHECKED | | | TITLE

APPROVED

DO NOT SCALE DRAWING

BREAK ALL SHARP EDGES AND

REMOVE BURRS
THIRD ANGLE PROJECTION

SIZE A | DWG NO. 4-0063 | REV.

SCALE 1:5 | WEIGHT | SHEET 1 of 1

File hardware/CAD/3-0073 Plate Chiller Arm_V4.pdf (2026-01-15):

2
1

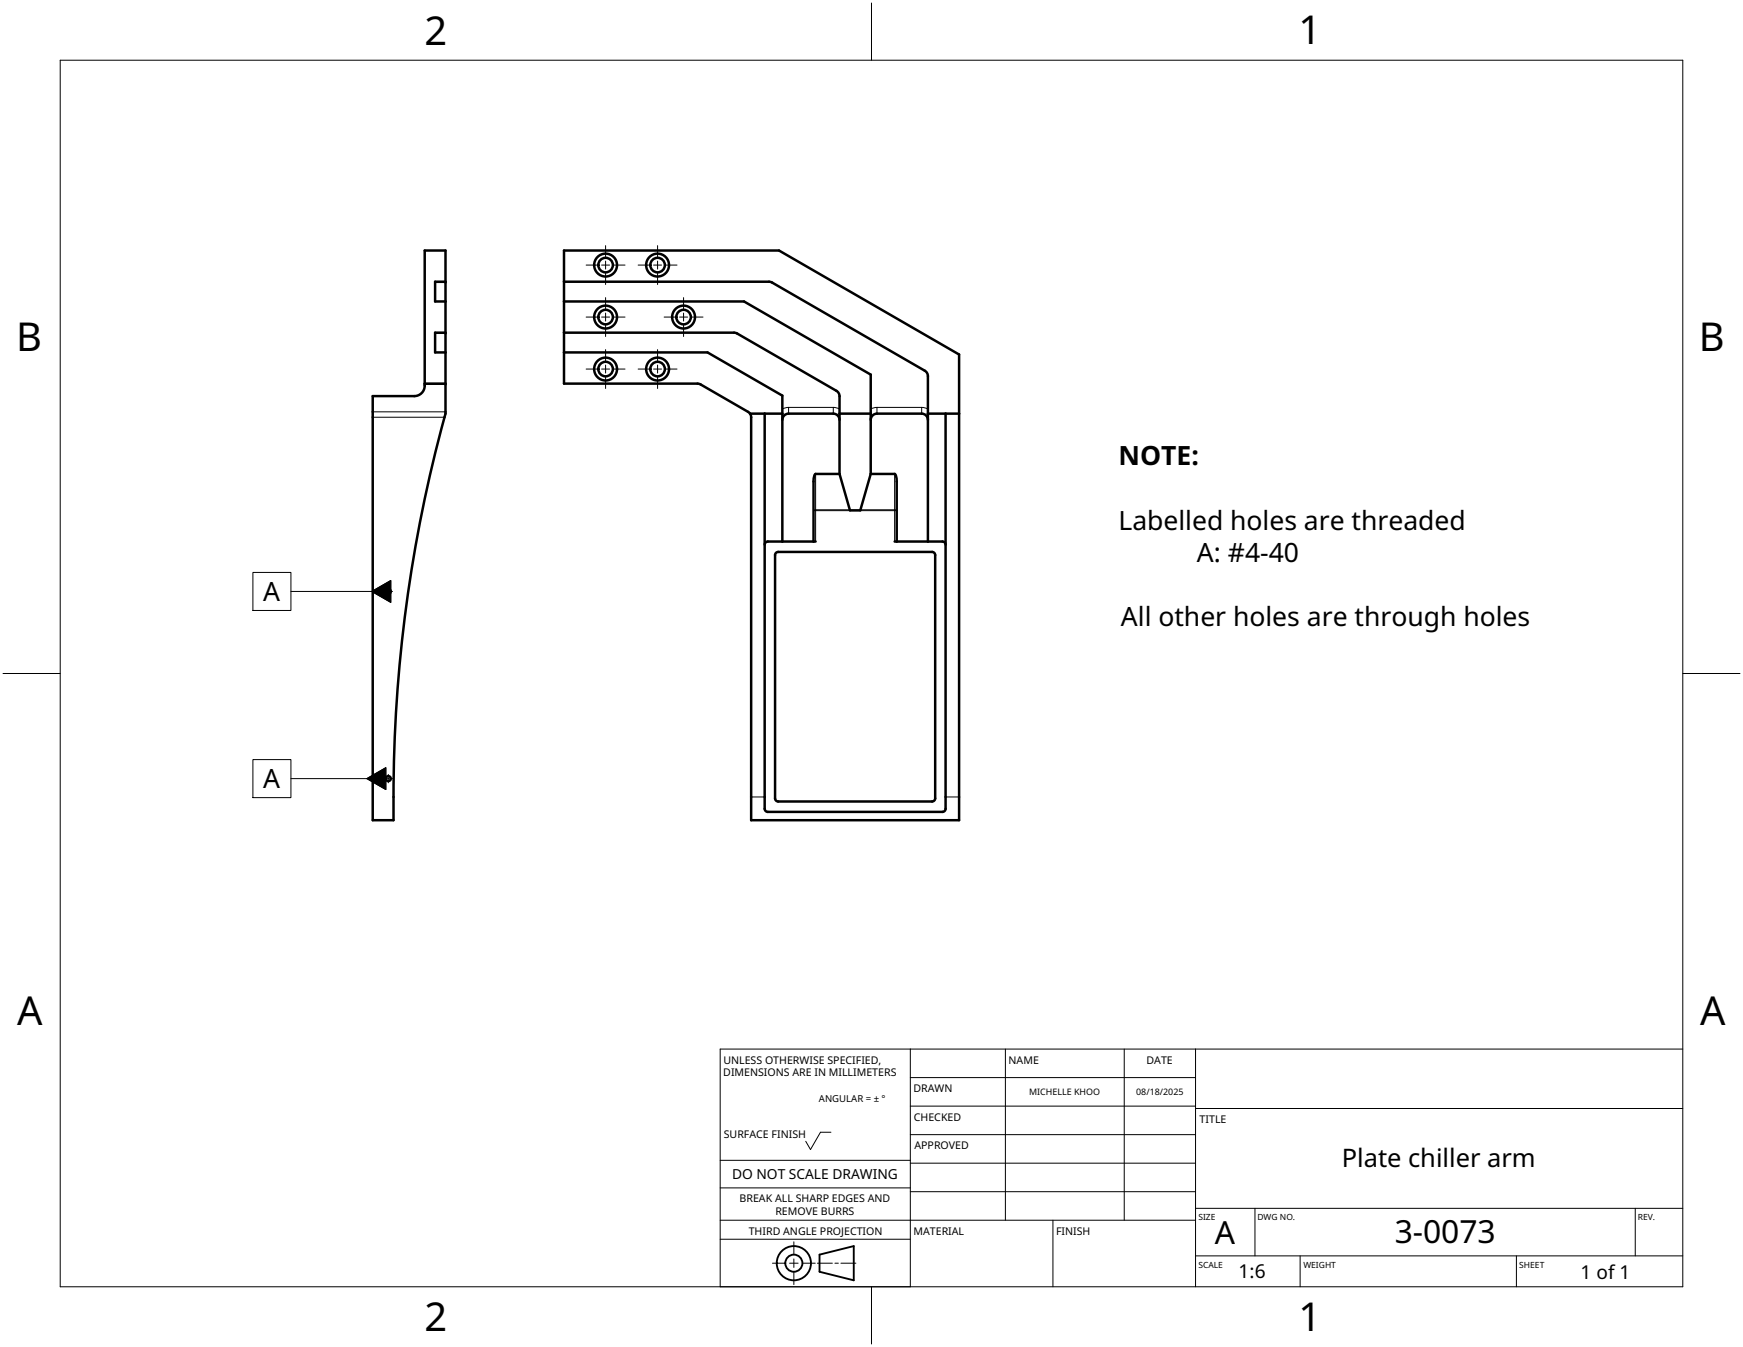
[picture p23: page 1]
MATERIAL; FINISH; NOTE:

Labelled holes are threaded

All other holes are through holes

UNLESS OTHERWISE SPECIFIED, DIMENSIONS ARE IN MILLIMETERS ANGULAR = ± ° SURFACE FINISH | | NAME | DATE

DRAWN | MICHELLE KHOO | 08/18/2025

CHECKED | | | TITLE Plate chiller arm

APPROVED

DO NOT SCALE DRAWING

BREAK ALL SHARP EDGES AND

REMOVE BURRS
THIRD ANGLE PROJECTION

SIZE A | DWG NO. 3-0073 | REV.

SCALE 1:6 | WEIGHT | SHEET 1 of 1

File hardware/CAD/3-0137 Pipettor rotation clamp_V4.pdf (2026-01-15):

2
1

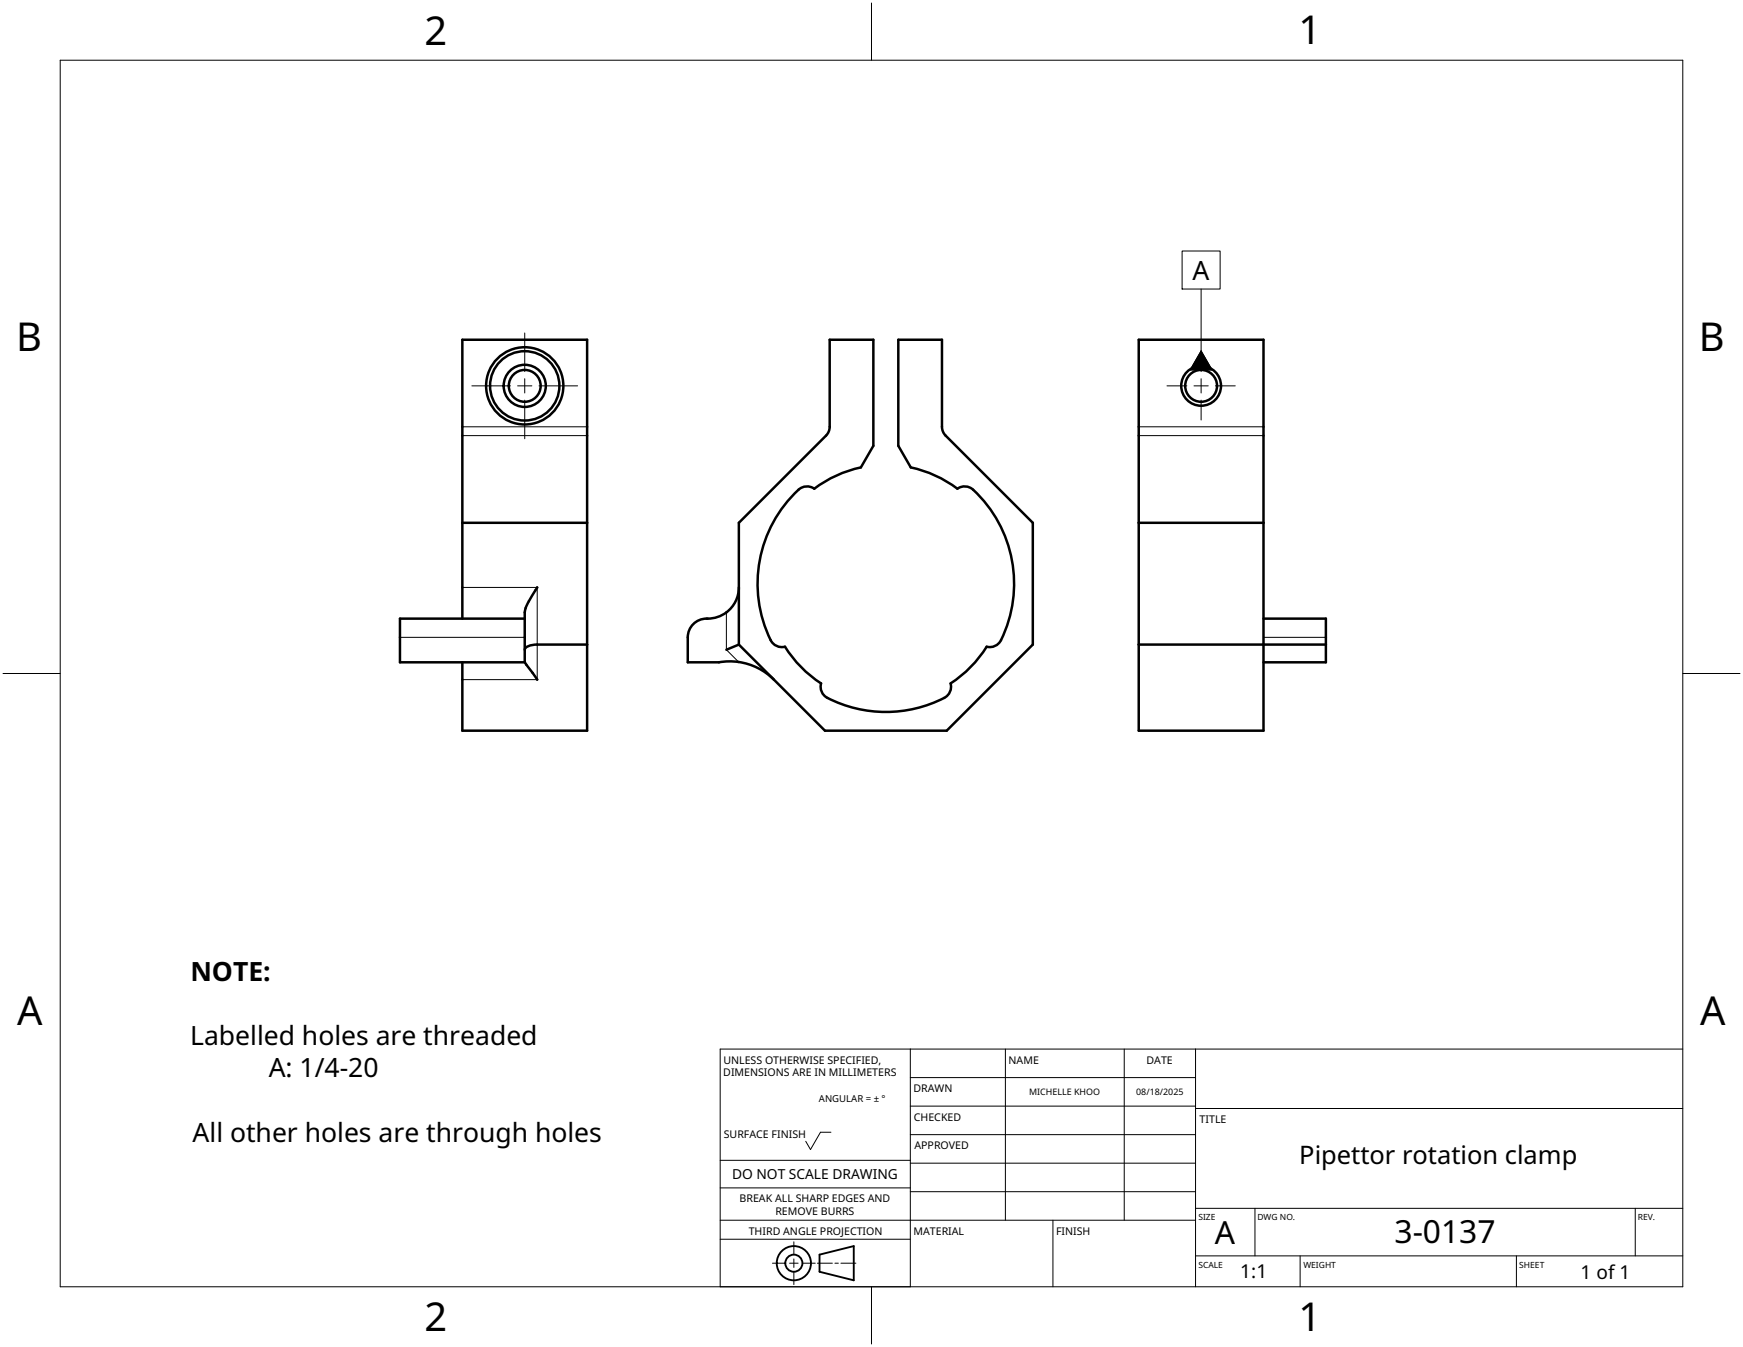
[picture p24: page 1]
MATERIAL; FINISH; NOTE:

Labelled holes are threaded

UNLESS OTHERWISE SPECIFIED, DIMENSIONS ARE IN MILLIMETERS ANGULAR = ± ° SURFACE FINISH | | NAME | DATE

DRAWN | MICHELLE KHOO | 08/18/2025

CHECKED | | | TITLE Pipettor rotation clamp

All other holes are through holes

APPROVED

DO NOT SCALE DRAWING

BREAK ALL SHARP EDGES AND

REMOVE BURRS
THIRD ANGLE PROJECTION

SIZE A | DWG NO. 3-0137 | REV.

SCALE 1:1 | WEIGHT | SHEET 1 of 1

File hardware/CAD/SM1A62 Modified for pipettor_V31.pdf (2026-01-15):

2
1

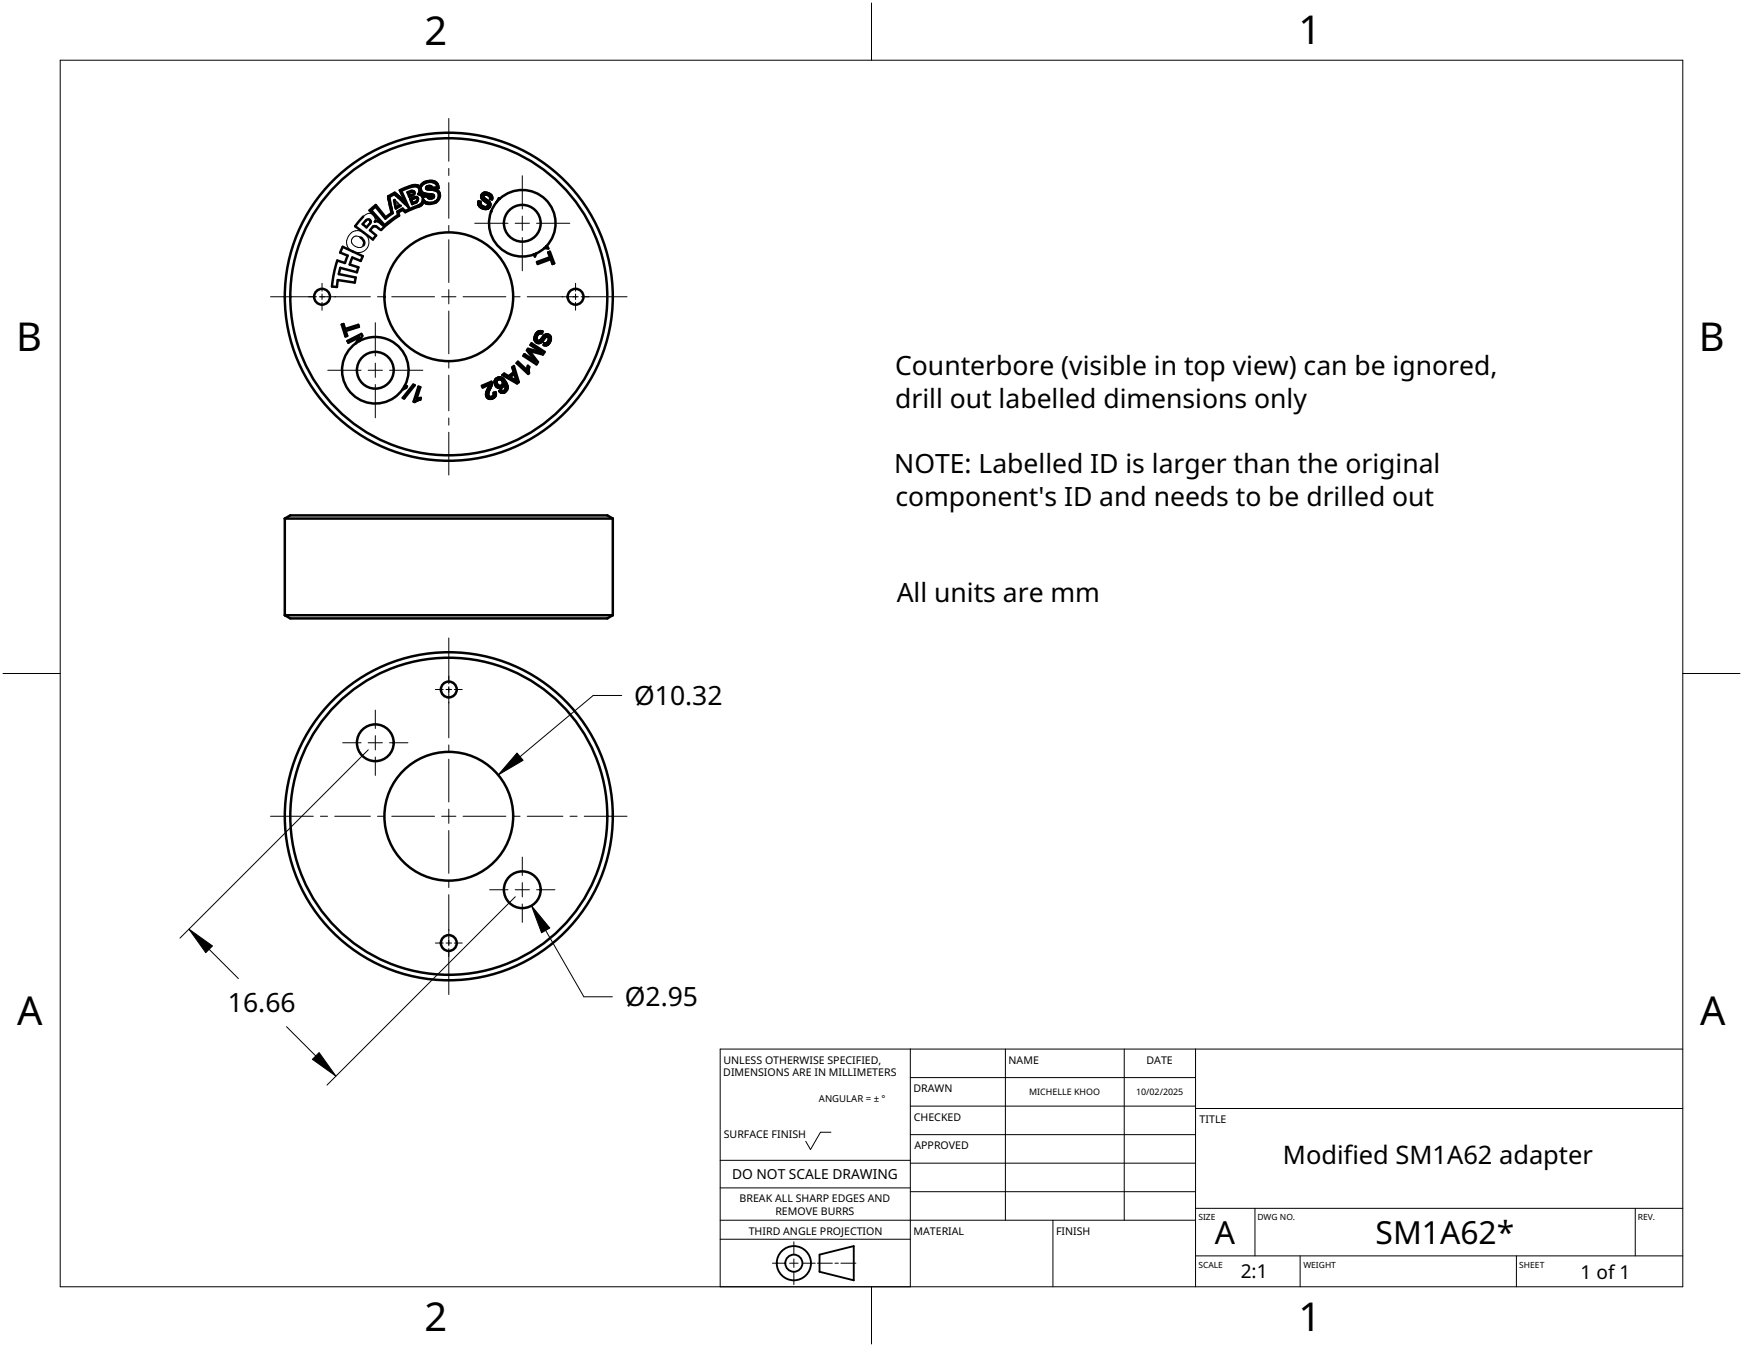
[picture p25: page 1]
MATERIAL; FINISH

Counterbore (visible in top view) can be ignored,
drill out labelled dimensions only

NOTE: Labelled ID is larger than the original
component's ID and needs to be drilled out

All units are mm

UNLESS OTHERWISE SPECIFIED, DIMENSIONS ARE IN MILLIMETERS ANGULAR = ± ° SURFACE FINISH | | NAME | DATE

DRAWN | MICHELLE KHOO | 10/02/2025

CHECKED | | | TITLE Modified SM1A62 adapter

APPROVED

DO NOT SCALE DRAWING

BREAK ALL SHARP EDGES AND

REMOVE BURRS
THIRD ANGLE PROJECTION

SIZE A | DWG NO. SM1A62* | REV.

SCALE 2:1 | WEIGHT | SHEET 1 of 1

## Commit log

2024-06-05 zaber initial commit
    added config files for zaber stage connections and locations and well plate definitions and positions
    build out of zaber controller
2024-07-25 add valve controller
2024-08-06 zaber stage updates for binary library
    - updated zaber class and config to control the stages with binary zaber library for legacy stages
    - created hardware test script to test zaber stages
2024-08-16 agarose array position generator
    -creates GUI to input the design parameters of the agarose mold and save a json file with the calculated positions and names for each well
    -saved two json position files for the embryo and larvae arrays currently in use
2024-08-21 Tested mapping and added plate loading/calibration
2024-08-21 Remove zaber stage reference for home
2024-08-21 Reformat json parsing to work with slot array files
2024-08-22 Add stage and plate calibration widget
2024-09-10 Test for valve controller
    Update valve controller test script based on registers for Wago valve controllers
2024-09-11 Valve Controller Class
    -Rewrote test of valve controller to start of the valve controller class
    -retained test of valve controller for troubleshooting
    -added to pneumatic_config the needed parameters
2024-09-13 Build up pipette controller class
    -Added functionality to valve controller class
    -Began building pipette controller class
    -Revised zaber controller class and all of the config files to better conform to structure
2024-10-07 picker test script
    -updates to pipette_gui.py to function with picker_config.json
2024-10-08 Updatenpipette_gui
    - Add functionality to pipette_gui to test picking_pipette.py class
2024-10-16 Pick workflow
    - Build out pick class to run through the full workflow from after classification to picking
    - Still have TODOs around handing mapping helper class to map between destination stage ID to coordinates
    - TODO around how to best handle offset pick locations from well center with respect to classification file
    - Potential future feature to sort pick list to snake through microscope positions to save time
2024-12-05 Note redundancy in picking pipette
2025-02-13 Basic napari-micromanager operation
    Update to enable basic napari-micromanager operation
    -Changes ones of the functions in the pipette test widget to move the stages over the objective to enable fluorescence imaging
2025-04-08 Valve Controller & Image Plate
    -Removed duplicate Image Plate instances and initialize Image Plate in main
    -Fix to Valve Controller to limit dropped connections
2025-04-11 Add Up Down buttons
    - Update Move Pipette function to have two buttons to move up or down instead of changing the value
2025-04-14 Added features from testing
    -Added autosave for mosaic layers
    -Added auto update & save for pipette height from calibration in config
    -Added scaling of sub images
2025-04-25 Classification GUI speed up & Pick GUI status
    -Added status for pick calibration
    -Fixes from testing with the revisions to speed up the classification GUI
2025-04-28 Inject function & update classify widgets
    -Added functionality for single injection testing of eggs for prototype dev
    -Add in embryo picking features
    -Remove Contrast widget loading, maintain contrast widget class in case it is desired in the future. Users natrually use the contrast adjustment in the native napari layers
    -Refocus viewer on fish finding widget after classification loaded
    -Update points layer specific key bindings so they map to old keybindings (single hand classification control
2025-05-30 Add hardware files/info
    [3-0053 SCP Pipettor L-bracket_V28.step, 3-0054 SCP Pipettor arm_V1.step, 3-0073 Plate Chiller Arm_V1.step, 3-0075 Non-piezo pipette holder_V1.STEP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]
2025-05-30 Add valve control
    [3-0053 SCP Pipettor L-bracket_V28.step, 3-0054 SCP Pipettor arm_V1.step, 3-0073 Plate Chiller Arm_V1.step, 3-0075 Non-piezo pipette holder_V1.STEP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]
2025-07-01 Start of split hardware and array init
    Start to split hardware controller and arrays initialization so that users can access the pipette hardware before inputting on arrays
    naming cleanup
2025-07-02 Update MM config for nrew filtersets
2025-07-03 Change Pick GUI & controller class init
    Change how the Pick GUI is initialized and buttons are enabled to allow for partial use of the hardware controller and picking class
    Hotfix to remove ability to delete points in classify
    Added fish counter to classify
    Change colors for different filters
    Added in new experiment option
    Adjust setup GUI spacing
2025-07-21 BF imaging, Pause, Classification features
    -Added Pause / Resume and Stop to picking thread
    -Added ability to better control BF imaging
    -Added classification fish finding for BF images (requires inverting threshold, and keeping BF data out of sum)
    -Added reset fish function to easily reset classification to empty
    -Changed well navigation to be able to navigate all wells, or those designated as singlets
2025-07-29 Change pick selection GUI loading to start
    -Moved pick selection GUI to setup so that if in the future automated classification is implemented it is ready
    -Found a bug and annoyance in the classification GUI, and fixed them. Bug was points could still be moved, even though that had been fixed before. It likely changed during the well loading speedup An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
    -Minor code cleanup
2025-08-01 Enable DAPI
    -Added DAPI filter set option, color map
    -Add pixel resolution to each magnification in MM
2025-12-16 Still init valve controller if zaber controller already exists
2025-12-18 Cleanup
    - Standardize to sorter from picker
    - Fix to outdated parameter for nmm_basic
    - Update SOP
    - add logging to file
    - Add part to hardware STEP files
    [3-1208_SCP Pipette stabilizer with short paddle_Main.step]
2025-12-19 Remove link to BOM in place of copy in repo
    Added Bill of Materials to README and updated links.
2025-12-19 Add fish sorter bill of materials
2026-01-13 Add pipette holder drawing
2026-01-13 Rename 3-0075 Non-piezo pipette holder_V5.pdf to 3-0075 Pipette holder_V5.pdf
2026-01-13 Update and rename 3-0075 Non-piezo pipette holder_V1.STEP to 3-0075 Pipette holder_V1.STEP
    [3-0075 Pipette holder_V1.STEP]
2026-01-13 Re-upload pipette holder .step
    [3-0075 Pipette holder_V1.STEP]
2026-05-11 Generalize file path handling and accept XY zaber stage with matching names
2026-06-10 Added error handling if not all stages connect
